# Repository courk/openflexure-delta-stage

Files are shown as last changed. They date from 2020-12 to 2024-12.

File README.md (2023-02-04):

# OpenFlexure Delta Stage

A 3D Printable high-precision 3-axis delta-bot translation stage.

This project is a 3D printable design that enables very fine (sub-micron) mechanical positioning of a small moving stage, with surprisingly good mechanical stability.  It follows on from the [OpenFlexure Microscope](https://openflexure.org/projects/microscope/). The main advantage of this design is that the optics remain in a fixed position, allowing more complex and heavier optics modalities, as well as coupling into external optics.  

We have described the OpenFlexure Delta Stage's design and possible optical configurations in [Optics Express](https://doi.org/10.1364/OE.450211).

## Printing and building it

The [Delta Stage home page](https://openflexure.org/projects/deltastage/) is the best place to start with making your own Delta Stage.

### Assembly instructions

The [assembly instructions](https://build.openflexure.org/openflexure-delta-stage/latest) contain all the STLs you need to download and print, and a bill of materials for the non printed parts.  There is also guidance on 3D printer settings.  

The assembly instructions give a step by step guide to building the Delta Stage, as both a translation stage and a complete microscope (transmission and reflection illumination).

## Software

The Delta Stage can be powered by [Raspbian-OpenFlexure](https://openflexure.org/projects/deltastage/build#install-the-os).  You can control the Delta Stage either on the Raspberry Pi itself or from a different computer using [OpenFlexure Connect](https://openflexure.org/projects/deltastage/install).

## Customising it

You can customise the delta stage to suit your application.  All of the designs are made using [OpenSCAD](https://www.openscad.org/). Currently we use [OpenSCAD 2019.05](https://openscad.org/news.html#20190518).

### Cloning the repository

The Delta Stage repository uses additional git features which can require extra steps. For this reason, it is recommended that you clone it, rather than download it.  

* The repository uses [submodules](https://git-scm.com/book/en/v2/Git-Tools-Submodules) to include parameters, objects and components from the [OpenFlexure Microscope repository](https://gitlab.com/openflexure/openflexure-microscope).

* The repository uses [git-lfs](https://git-lfs.github.com/) for version control of image (and other large) files. If git-lfs is not installed, cloning the repository will only download placeholders of these files.

#### Visual Studio Code

The easiest way to clone the repository is with [Visual Studio (VS) Code](https://code.visualstudio.com/), with [git-lfs installed](https://git-lfs.github.com/).  If you [clone the repository using VS Code](https://code.visualstudio.com/docs/editor/versioncontrol#_cloning-a-repository) these additional features should work automatically.

You can then make changes using VS Code and use OpenScad with the editor hidden and the `automatic reload and compile` option ticked for compiling.

#### Cloning using the command line

1. Download and install [git-lfs](https://git-lfs.github.com/).

2. The easiest way to correctly clone the project is to run:

    ```bash
    git clone --recurse-submodules https://gitlab.com/openflexure/openflexure-delta-stage.git
    ```

    If the `openflexure-microscope` folder is empty, you should run the following in the main `openflexure-delta-stage` folder:
    1. `git submodule init` (to set the repository up for the first time).
    2. `git submodule update` (to fetch the required data).

 > With git-lfs installed, git will download the latest version of the large files.  If they are still missing run:

```bash
git lfs fetch 
git lfs checkout
```

  > To make Git always download everything in the repository run the following commands in your terminal:

```bash
git config --local lfs.fetchexclude ""
git lfs fetch
git lfs checkout
```

### Downloading the repository

1. Download the `openflexure-delta-stage` repository.
2. In the OpenFlexure Delta Stage repository on GitLab, click on the 8 characters (the commit ref) after the `@` on the folder named `openflexure-microscope @ ...`. This will take you to the OpenFlexure Microscope repository at the correct commit.
     > :warning: It is important that the submodule is at the correct commit, it will not work if it is on a different commit.
3. Download the OpenFlexure Microscope repository and copy these files in the folder called `openflexure-microscope` in the Delta Stage folder.

### Guide to repository

#### Delta Stage components

The Delta Stage components are found in the `openscad` folder. For example the main body is compiled from `openscad/delta_stage.scad`.  The majority of parameters reside in `openscad/parameters.scad`, so you can easily change aspects of the design (height etc.). Some parts of the design borrow objects from the `openflexure-microscope` submodule.

> :warning: There are currently issues where OpenSCAD runs out of memory when previewing or compiling `delta_stage.scad` in the graphical interface. The complexity of the model will be reduced to fix this, but in the meantime it is still possible to compile it using the [command line](https://en.wikibooks.org/wiki/OpenSCAD_User_Manual/Using_OpenSCAD_in_a_command_line_environment#Command_line_usage):

```bash
openscad -o delta_stage.stl delta_stage.scad
```

#### OpenFlexure Microscope components

The `openflexure-microscope` folder is a submodule containing a version of the [OpenFlexure Microscope repository](https://gitlab.com/openflexure/openflexure-microscope) at a specific commit. The components common to both devices are compiled from there.  If you make changes to these components that you feel should be merged in for others to use, then you should make a merge request to that repository (bearing in mind that it will be ahead of the specific commit that this repository uses).

#### Building the components

To build every component you can run ``build.sh`` if you have a Bash shell (in either linux or Windows Subsystem Linux).  You may need to add ``openscad`` to your path if you want this to work in MinGW on Windows, or in the Mac OS Terminal.

It is also useful to look in ``build.sh`` to see how the components are compiled (and from which OpenSCAD file) as some use command line variables.

#### Writing assembly instructions

The [assembly instructions](https://build.openflexure.org/openflexure-delta-stage/latest) cover the standard uses for the delta stage. They are compiled using [gitbuilding](https://gitbuilding.io/) and stored in the `\docs` folder.

### Release flow

We use the [OpenFlexure workflow](https://openflexure.org/contribute/) for development.

We use GitLab CI to manage builds and deployment.

The CI will build STL files that will remain on GitLab for 1 week when:

* A merge request is submitted
* A merge request is modified

The CI will build and deploy STL files and documentation to [build.openflexure.org](https://build.openflexure.org/openflexure-delta-stage) when:

* A build is manually triggered from GitLab web
* A release is tagged

The build server will mark a release as "latest"( [build.openflexure.org/openflexure-delta-stage/latest](https://build.openflexure.org/openflexure-delta-stage/latest) ) when a release is tagged, with a full semantic version and no suffix. For example:

* v6.0.0 will replace "latest"

However, incomplete semantic versions will not replace latest. For example:

* v6.0.1-beta.1 will **not** replace "latest" (pre-release suffix)
* v6.1 will **not** replace "latest" (no patch version specified)
* 6.0.1a will **not** replace "latest" (non-standard suffix)

## Get Involved

It'll be great if you are able to contribute to the OpenFlexure Delta Stage. If you have any issues, questions or suggestions we would love to hear them.

You can:

* Join the discussion in the [forum](https://openflexure.discourse.group/).
* Make an [issue](https://gitlab.com/openflexure/openflexure-delta-stage/-/issues/new).
* Make a merge request.
* [Tweet us](https://twitter.com/openflexure) with your completed projects.

## License

This project is open-source and is released under the CERN open hardware license.  There is not yet any accompanying software, but if that changes please consider it GPL.  Any documentation contained in this project is licensed CC-BY International 4.0.  We are working on selling kits through OpenFlexure Industries, though we're not yet taking orders - however this will stay a fully open-source project.

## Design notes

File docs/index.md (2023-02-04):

# OpenFlexure Delta Stage

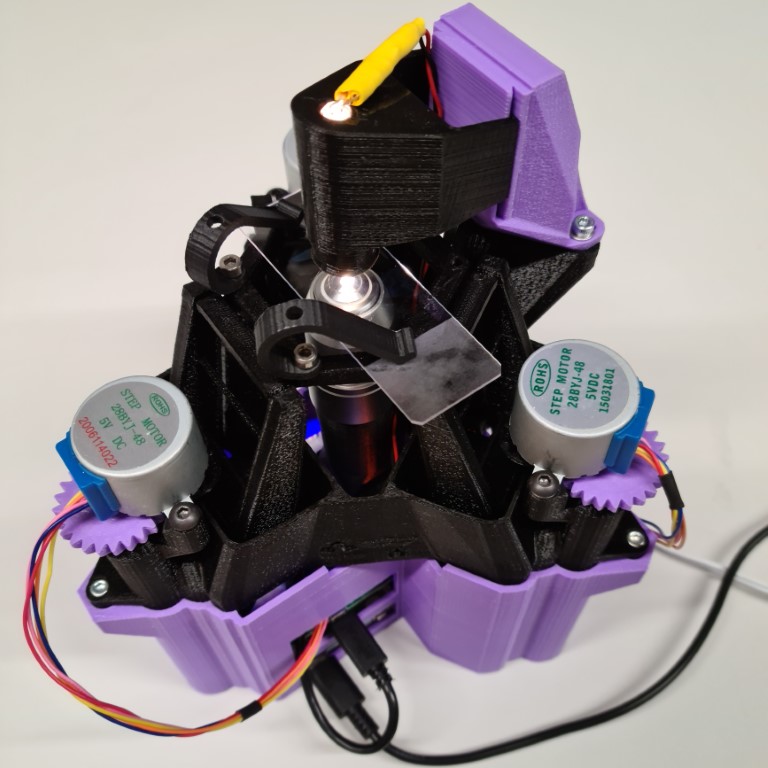
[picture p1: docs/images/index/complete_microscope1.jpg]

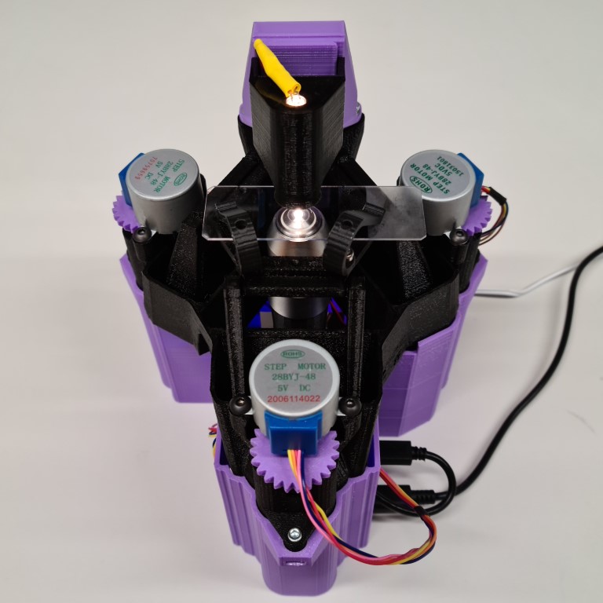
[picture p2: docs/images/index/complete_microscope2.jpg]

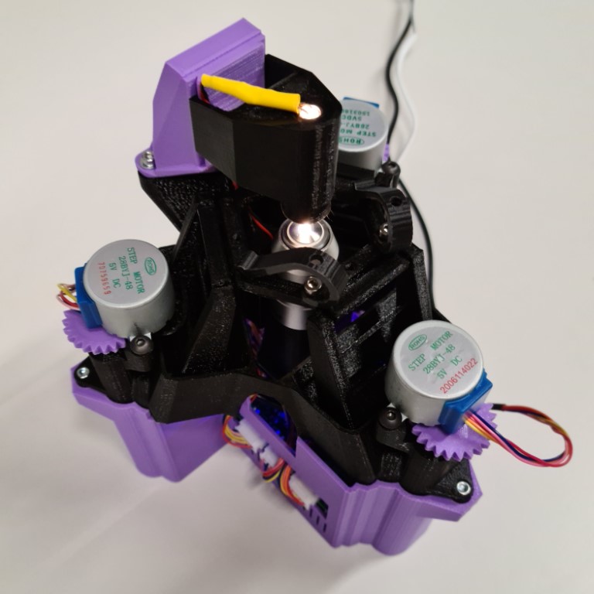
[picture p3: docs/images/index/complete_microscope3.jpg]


The delta stage is a 3D printed x-y-z translation stage. As the optics do not move it is particularly suited to more complex imaging (phase, reflection, fluorescence microscopy).  There are two standard ways to build it, with either transmission illumination or reflection illumination.  The motorised translation stage, which forms the main body of the microscope, is the same for both, and so swapping between the two configurations is possible by replacing the optics module.  There are also some optional components linked at the bottom of the page.

## Publications

We have described the OpenFlexure Delta Stage's design and possible optical configurations in [Optics Express](https://doi.org/10.1364/OE.450211). You can find more related publications and media articles on the [OpenFlexure website](https://openflexure.org/about/media-publications).

## Printing guidance

We normally print with PLA using a 0.15 layer height and ~18% infill. You should not need to print any of the parts with adhesion settings (brim etc.) or supports.  Take note of the optics parts we recommend you print with black PLA, to reduce stray light.

## Building the Delta Stage

There are two versions of the instructions:

* [Delta stage microscope with transmission illumination](pages/index_transmission.md)
* [Delta stage microscope with reflection illumination](pages/index_reflection.md)

### Optional components

* [Simple base](pages/simple_base.md):  Base with nothing inside; matches the footprint of the OpenFlexure Delta stage exactly.
* [Infinity corrected transmission optics module casing](models/optics_picamera2_rms_infinity_f50d13_delta.stl){previewpage}: If you are using infinity corrected objective lenses, you will need to use this version of the optics module casing.  
* [Stage adapters](pages/stage_adapters.md): Adapters for the stage to hold different components.
* [LED Grid illumination](pages/LED_grid_illumination.md): For more complex illumination.

### Software

You can control your microscope using the [OpenFlexure software](https://openflexure.org/projects/microscope/install). The geometry of the Delta Stage is different to the standard OpenFlexure Microscope.  So that the movement of the stage is correct, you will need to change the stage configuration:

1. In OpenFlexure Connect, when connected to your Delta Stage microscope, click `Settings`.
2. Under `MICROSCOPE SETTINGS`, click `Stage`.
3. Change the `Stage geometry` dropdown to `SangaStage (Delta)`.
4. Click `CHANGE STAGE GEOMETRY`.

## Design notes

* [Stage geometry](pages/stage_geometry_notes.md)

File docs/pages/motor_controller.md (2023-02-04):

# Motor controller (Sangaboard)

The stage can be powered by a Raspberry Pi and a motor controller.

{{BOM}}

[Raspberry Pi power supply]: ../components/raspi_power.md "{cat:part}"
[red 4A instrument wire]: ../components/4A_instrument_wire.md#red "{cat:part}"
[black 4A instrument wire]: ../components/4A_instrument_wire.md#black "{cat:part}"
[4.8mm heat shrink]: ../components/4_8mm_heat_shrink.md "{cat:part}"
[6.4mm heat shrink]: ../components/6_4mm_heat_shrink.md "{cat:part}"
[soldering iron]: "{cat:tool}"
[wire stripper]: "{cat:tool}"
[craft knife]: "{cat:tool}"
[heat gun]: "{cat:tool}"
[wire cutters]: "{cat:tool}"

# Method

## The Sangaboard {pagestep}

[These instructions](https://build.openflexure.org/openflexure-microscope/v6.1.5/docs/#/6_motor_controllers) show the different ways of controlling the motors. The base currently works with the Sangaboard v0.2 and v0.3.

## Powering the motors for Sangaboard v0.2 {pagestep}

Do not power the motors from the pins on the Raspberry Pi.  Instead split the [Raspberry Pi power supply] cable.  

Cut the [Raspberry Pi power supply]{qty:1} cable approximately 20cm from the USB plug end using [wire cutters]{qty:1}.

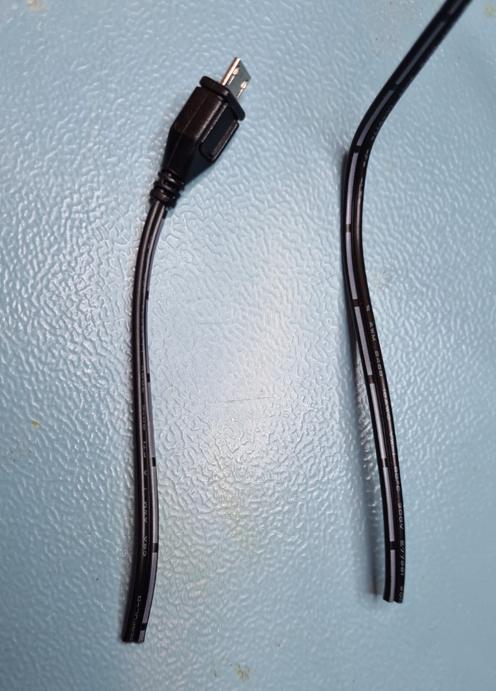
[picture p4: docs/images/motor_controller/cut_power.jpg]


Carefully separate the two cables using a [craft knife]{qty:1} on the USB plug cable for approximately 3cm and strip both wires using a [wire stripper]{qty:1}. Check which wire is positive and negative.  On this official [Raspberry Pi power supply] cable, the wire with long lines printed on is the negative wire.

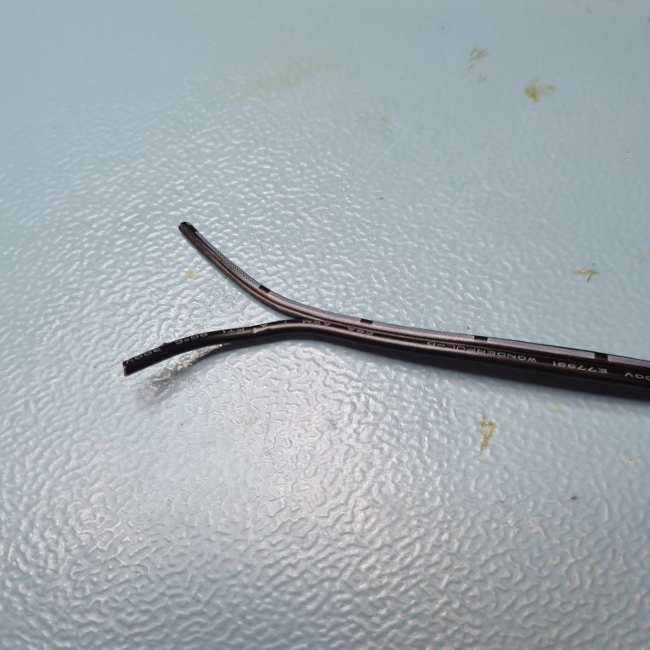
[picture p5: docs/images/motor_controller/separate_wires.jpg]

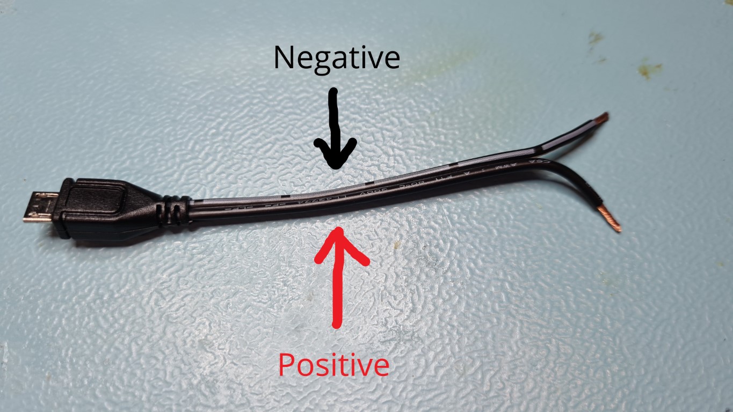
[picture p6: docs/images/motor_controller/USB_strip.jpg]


Cut a 20cm length of [red 4A instrument wire]{qty:20cm} and [black 4A instrument wire]{qty:20cm} using [wire cutters]{qty:1}. Strip one end using a [wire stripper]. Wrap the red wire around the positive wire of the [Raspberry Pi power supply] cable. Solder in place with a [soldering iron]{qty:1} and [solder]{qty:some}.

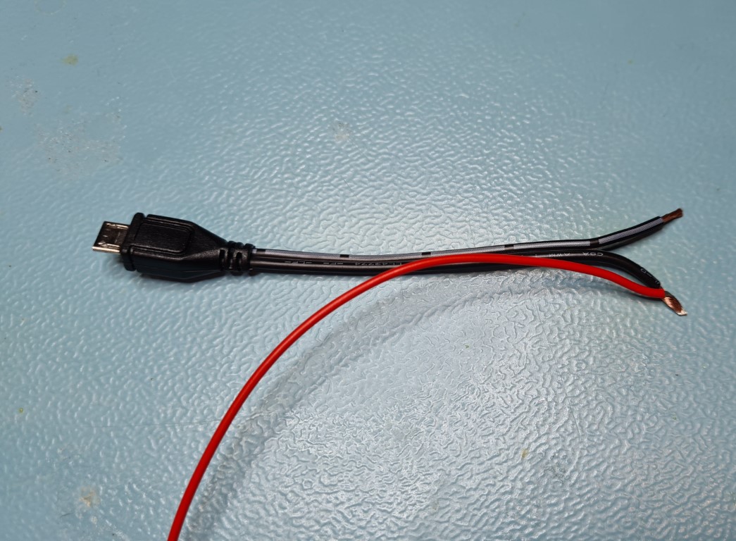
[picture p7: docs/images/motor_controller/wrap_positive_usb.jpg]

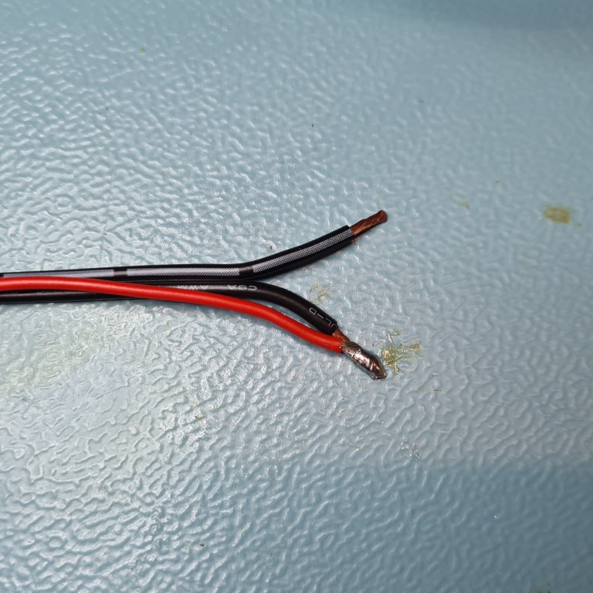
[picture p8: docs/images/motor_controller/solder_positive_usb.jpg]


Repeat for the [black 4A instrument wire] on the negative wire of the [Raspberry Pi power supply] cable.

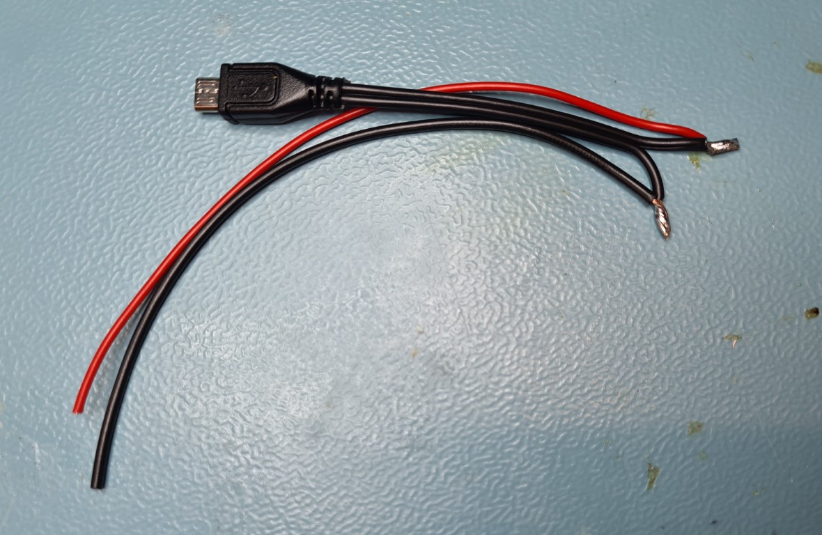
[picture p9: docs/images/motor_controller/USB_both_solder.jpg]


Cut two [4.8mm heat shrink]{qty:6cm} tubes approximately 3cm long.  Cut one [6.4mm heat shrink]{qty:6cm} tube approximately 6cm long.

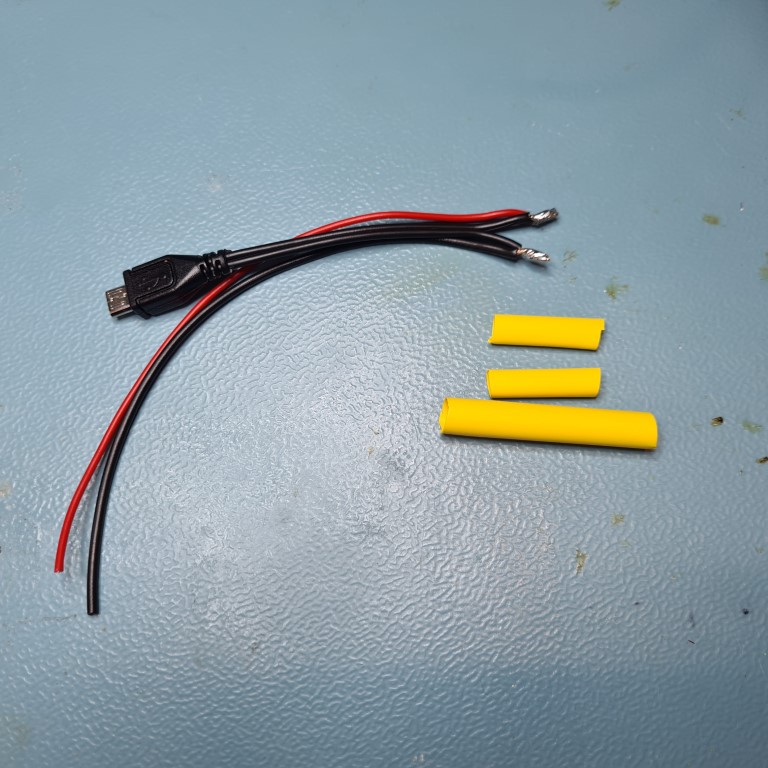
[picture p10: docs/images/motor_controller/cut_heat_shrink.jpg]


Carefully separate the two cables using a [craft knife]{qty:1} on the longer end of the [Raspberry Pi power supply] cable for approximately 5cm and strip both wires using a [wire stripper]. Push the longer [6.4mm heat shrink] tube over both wires and the two shorter [4.8mm heat shrink] tubes over each of the wires.

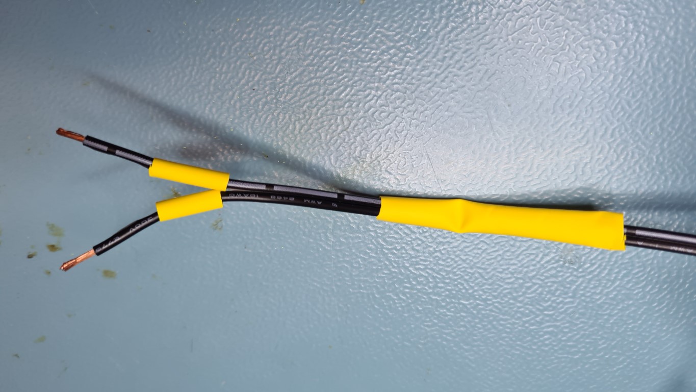
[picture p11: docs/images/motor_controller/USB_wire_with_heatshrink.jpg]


Wrap the negative wire from the longer cable with the already soldered negative wire from the USB end.  Solder in place with a [soldering iron]{qty:1} and [solder]{qty:some}.

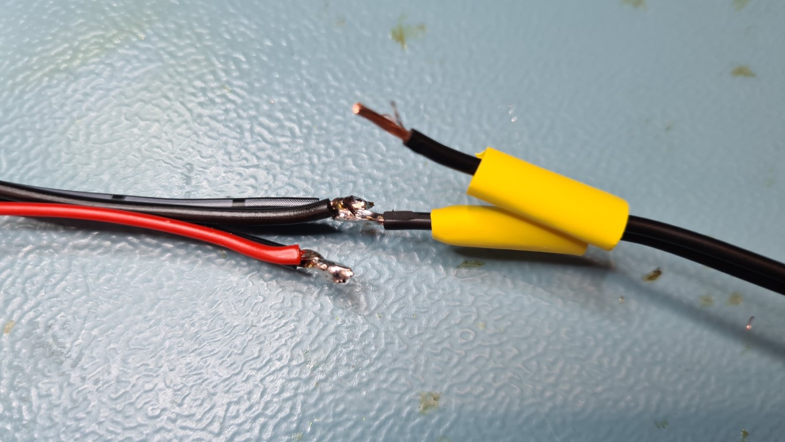
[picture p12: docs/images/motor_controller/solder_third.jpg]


Repeat for the positive wire.

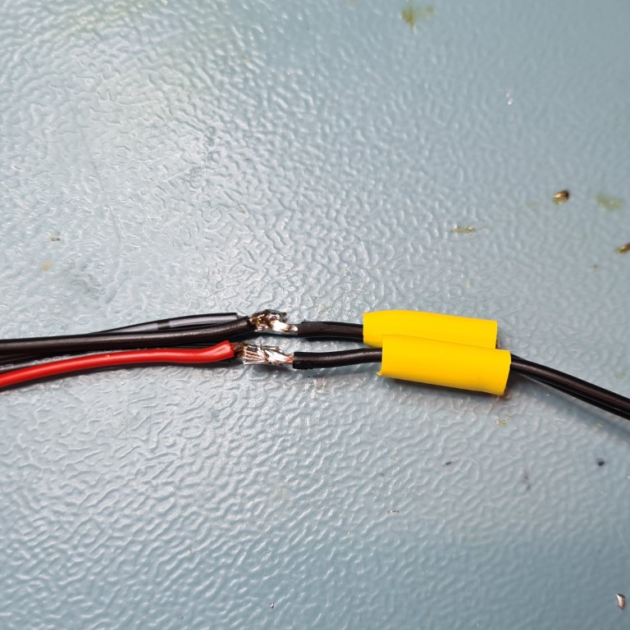
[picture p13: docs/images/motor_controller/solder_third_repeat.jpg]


Move the two [4.8mm heat shrink] tubes over the joints and heat in place using a [heat gun]{qty:1} or [soldering iron]{qty:1}.

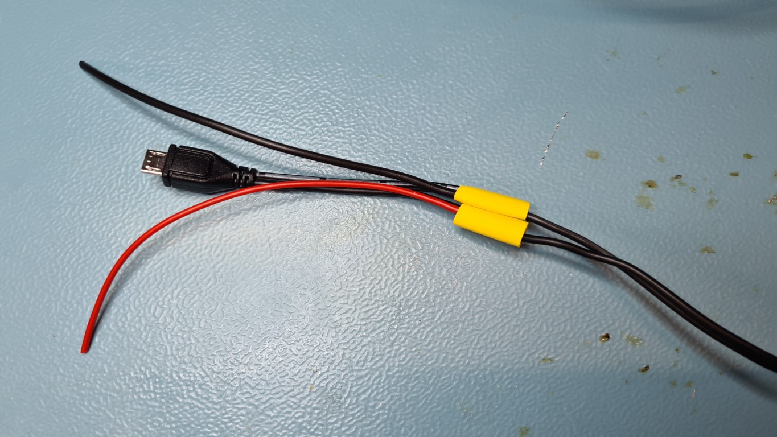
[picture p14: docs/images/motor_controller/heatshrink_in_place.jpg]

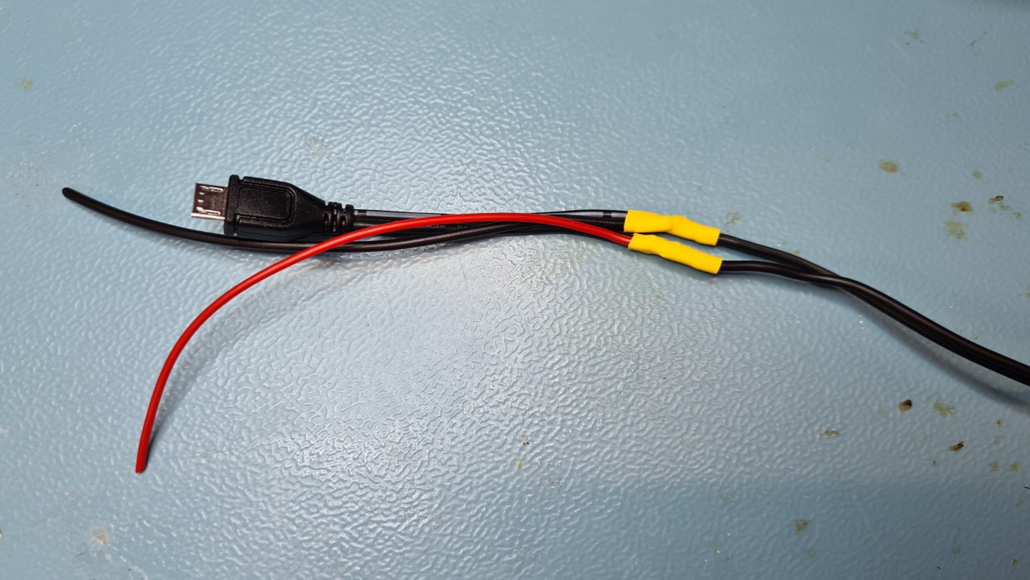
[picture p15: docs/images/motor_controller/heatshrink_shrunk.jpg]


Move the [6.4mm heat shrink] tube over both joints and heat in place using a [heat gun]{qty:1} or [soldering iron]{qty:1}.

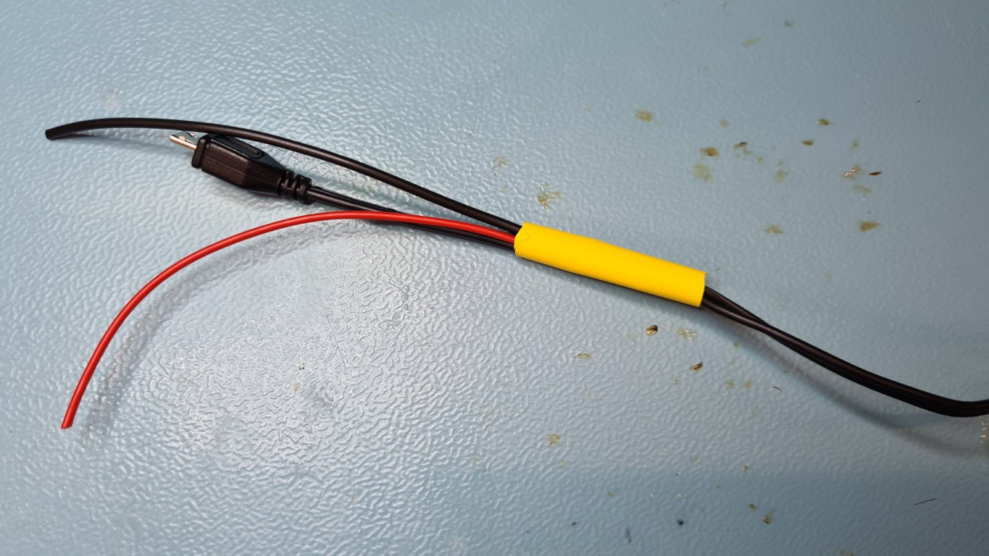
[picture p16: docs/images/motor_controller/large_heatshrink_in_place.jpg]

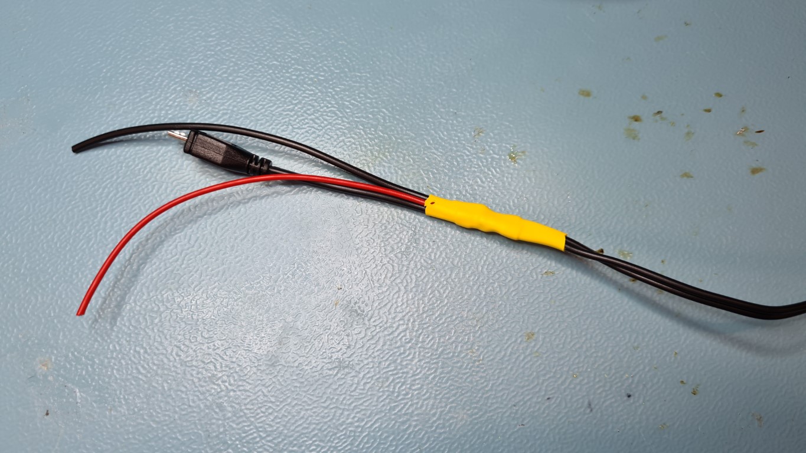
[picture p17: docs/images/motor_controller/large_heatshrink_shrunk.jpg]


You can then attach the connector of your choice to connect to the Sangaboard v0.2.

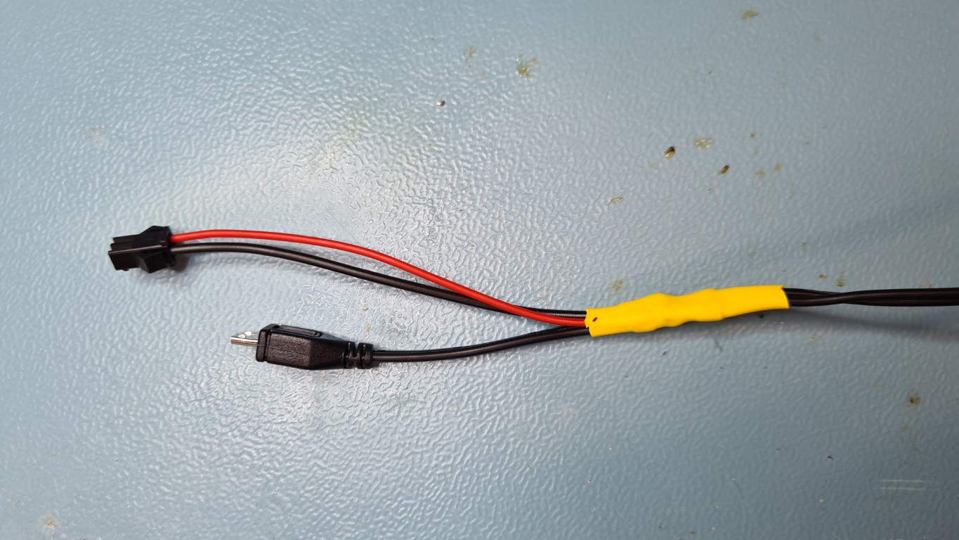
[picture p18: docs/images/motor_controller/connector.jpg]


## Powering the motors for Sangaboard v0.3 {pagestep}

The Sangaboard v0.3 is powered by micro USB.  It should not be powered from a USB port on the Raspberry Pi, but by a separate power source.

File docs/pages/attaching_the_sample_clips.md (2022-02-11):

# Attaching the sample clips

To securely hold a microscope slide on the stage, you can attach the sample clips.

{{BOM}}

[sample clip]: ../models/sample_clips.stl "{cat: 3DPrinted, note: Both sample clips are in the one file.}"
[M3x6mm screw]: "{cat:part}"

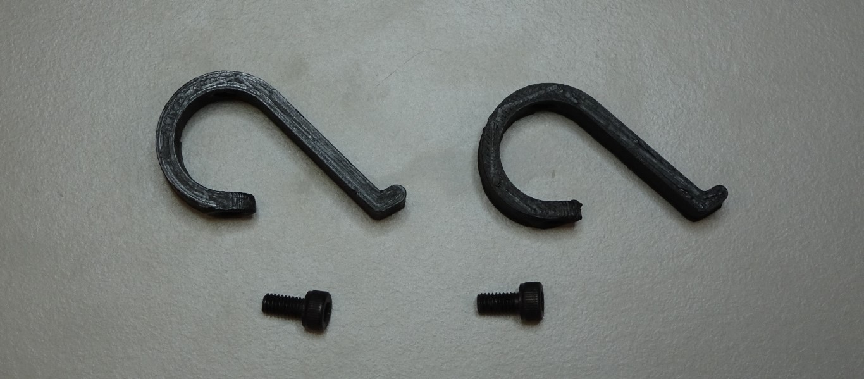
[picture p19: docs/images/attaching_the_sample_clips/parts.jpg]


[2.5mm hex screwdriver]: "{cat:tool}"

# Method

## Insert the screws into the clips {pagestep}

Push the two [M3x6mm screw]{qty:2}s through the lower hole of the [sample clip]{qty:2} using a [2.5mm hex screwdriver]{qty:1}.  

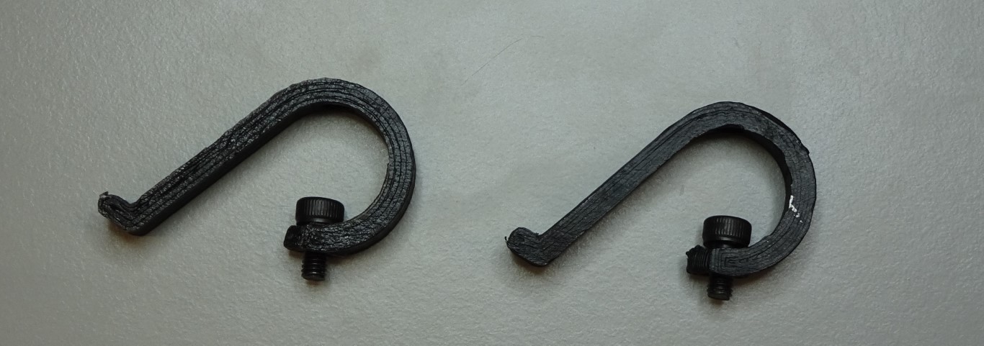
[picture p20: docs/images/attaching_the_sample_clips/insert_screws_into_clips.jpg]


## Screw the sample clips onto the stage {pagestep}

There are 9 holes on the top of the stage, allowing you flexibility when choosing where to place the sample clips. Screw the sample clip to the stage, going through the hole at the top.  

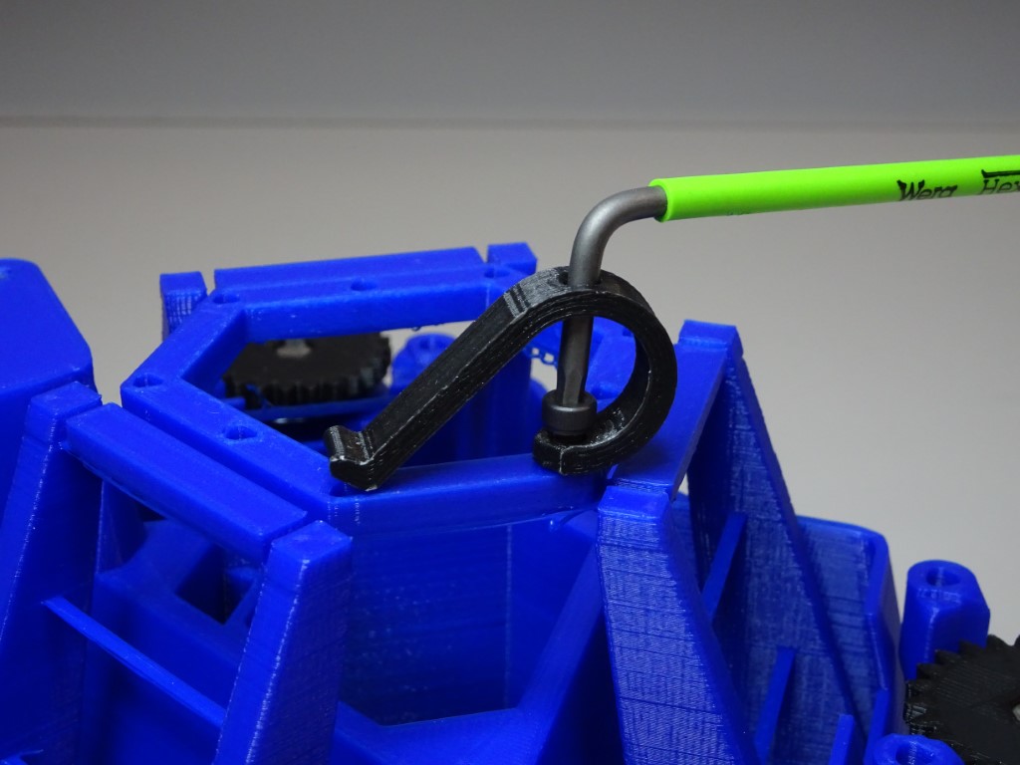
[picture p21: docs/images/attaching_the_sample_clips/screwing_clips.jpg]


If it is difficult to start screwing, then you may find it useful to tap the hole with the screw first.  

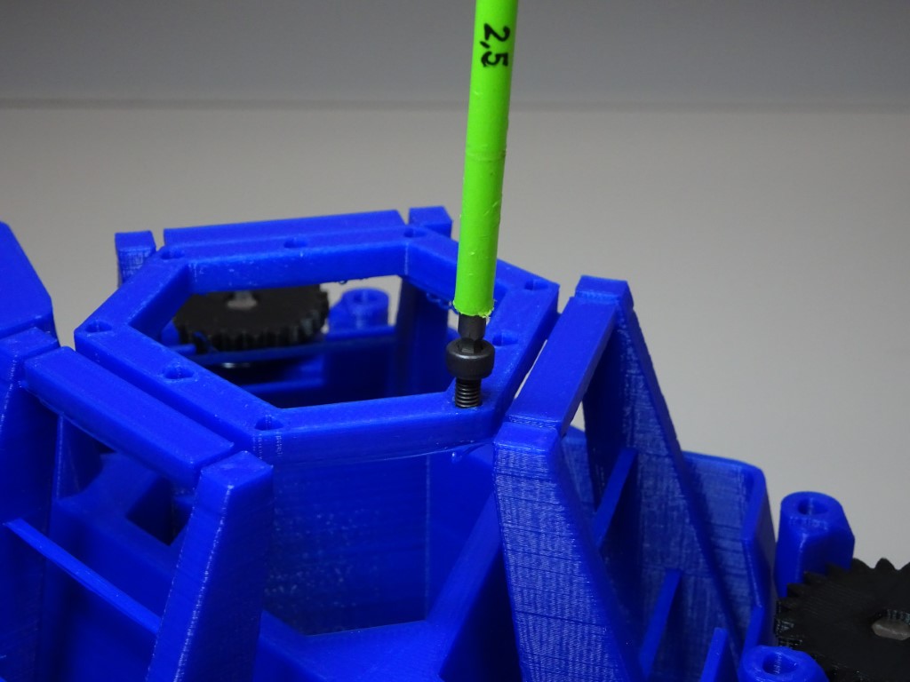
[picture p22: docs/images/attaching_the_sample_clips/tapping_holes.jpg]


Attach the second clip in the same way.  

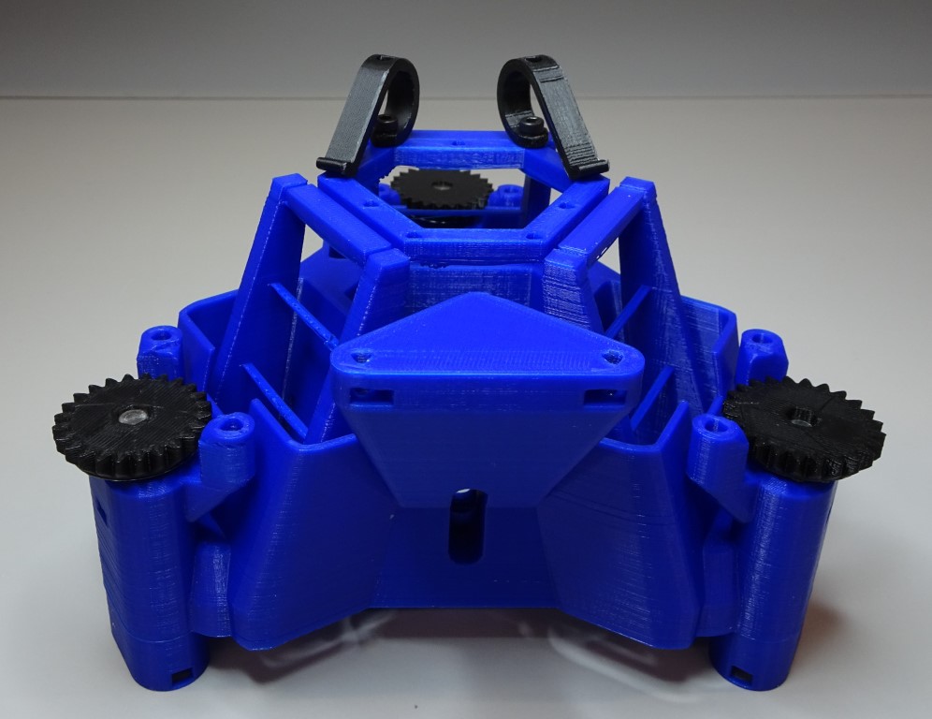
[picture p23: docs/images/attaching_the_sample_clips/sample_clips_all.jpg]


## Clamp the slide {pagestep}

Now you can gently lift up the glass clips and place your microscope slide.  

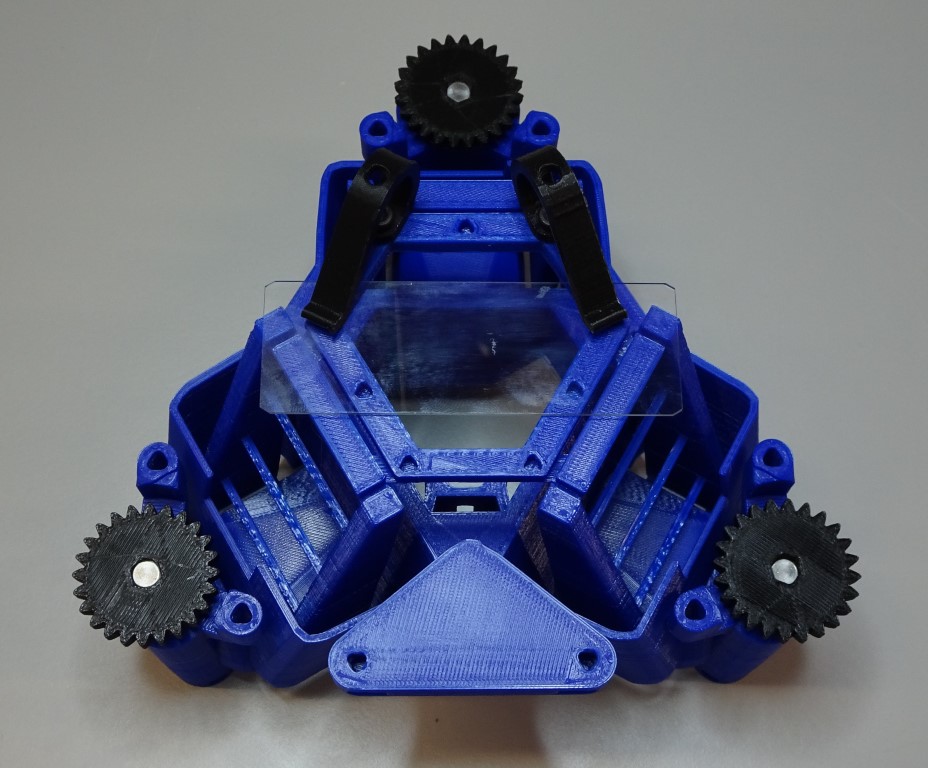
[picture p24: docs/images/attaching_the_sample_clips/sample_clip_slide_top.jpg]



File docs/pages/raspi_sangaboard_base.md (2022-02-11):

# Raspberry Pi and Sangaboard base

This base fits both the Raspberry Pi (Models B+, 2, 3B, 3B+, 4B) and the Sangaboard (v0.2 and v0.3), with holes for the wires and connections and space for an optics module to move.

>**Warning:** Make sure your SD card is flashed with the [OS and software](../index.md#Software) and inserted into your Raspberry Pi.

{{BOM}}

[Raspberry Pi & Sangaboard base]: ../models/base_raspi_sangaboard.stl "{cat: 3DPrinted}"
[M2.5x20mm standoff]: ../components/20mm_standoffs.md "{cat:part}"
[M2.5x8mm screw]: "{cat:part}"
[M3x12mm screw]: "{cat:part}"
[M3 nut]: "{cat:part}"
[Raspberry Pi]: ../components/raspberry_pi.md "{cat:part}"
[Sangaboard]: ../components/sangaboard.md "{cat:part}"
[USB cable]: ../components/sangaboard_USB_cable.md "{cat:part}"
[main body]: ../components/delta_stage_main_body.md "{cat:3DPrinted}"
[small pliers]: "{cat:tool}"
[SW5 nut driver]: "{cat:tool}"
[2mm hex screwdriver]: "{cat:tool}"
[2.5mm hex screwdriver]: "{cat:tool}"

# Method

## Base stabilisation {pagestep}

You may wish to add [rubber feet]{qty:3} to your [Raspberry Pi & Sangaboard base]{qty:1} for stability.




Alternatively, you could sit it on a layer of foam or drill holes in the bottom of the base to attach it to an optical bench.

## Add Raspberry Pi {pagestep}

Connect the camera ribbon cable and LED to the [Raspberry Pi]{qty:1}. The LED should connect with the positive (red) cable to the 5V pin (number 4) and the ground (black) cable to the Ground pin (number 6) on the [GPIO](https://www.raspberrypi.org/documentation/usage/gpio/).

Place the [Raspberry Pi] into the bottom of the case.  Screw the four [M2.5x20mm standoff]{qty:4}s through the holes of the Raspberry Pi (hand tight or using [small pliers]{qty:1} or [SW5 nut driver]{qty:1}, being careful not to over-tighten) and into the base.  You may find it easier to tap the holes with M2.5 screws before.




## Add Sangaboard {pagestep}

Place the [Sangaboard]{qty:1} on top of the standoffs, making sure the cables from the Raspberry Pi have space. The LED cable can exit the through the window at the back.  

### Sangaboard v0.2

Screw the [M2.5x8mm screw]{qty:4}s using a [2mm hex screwdriver]{qty:1} through the holes of the Sangaboard into the standoffs. You might find it easier to attach all four loosely, then tighten them together. Be careful not to over-tighten these screws.





### Sangaboard v0.3

You can attach this Sangaboard to the two standoffs closest to the GPIO with two [M2.5x8mm screw]s using a [2mm hex screwdriver]{qty:1}.  It will sit (but not secured) on the other two standoffs.




## Plug in motors {pagestep}

Plug in the motors.  Motor cables from motors `a` and `b`  can enter though the window in the side of the case and the motor cable from motor `c` can enter through the window at the back or the side. The correct order to plug in the motors can be seen here:

### Sangaboard v0.2




### Sangaboard v0.3




(For other motor controllers: `a = x`, `b = y`, `c = z`)

## Attach the camera ribbon cable {pagestep}

Connect the ribbon cable to the camera module.



## Put microscope into base {pagestep}

The microscope [main body] fits tightly into the [Raspberry Pi & Sangaboard base].



## Secure the microscope to the base {pagestep}

Insert one [M3 nut]{qty:3} into the nut trap in the base.  It may be necessary to clear out the hole of printing artefacts.  




Insert one [M3x12mm screw]{qty:3} into the hole in the microscope [main body].  Screw it in place using a [2.5mm hex screwdriver]{qty:1}.





Repeat for the other two base connectors.





## Connect the Sangaboard {pagestep}

The Sangaboard connects to the Raspberry Pi from the Arduino USB port by [USB cable]{qty:1}. There is a special window for the USB cable to pass through.

### Sangaboard v0.2




### Sangaboard v0.3





## Attach external components {pagestep}

There are windows around base to connect external components.  On the side there is space for USB power to the Raspberry Pi and Sangaboard v0.2 and HDMI.




At the back there is space for USB components (for example: keyboard, mouse, memory stick), ethernet and power supply for the Sangaboard v0.3.




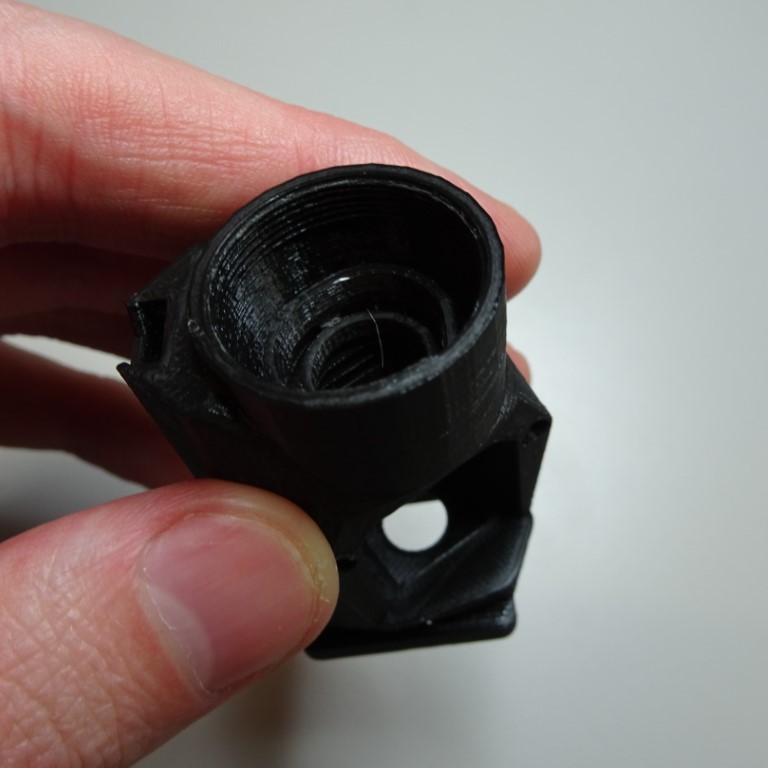
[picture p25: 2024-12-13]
docs/images/reflection_illumination/clean_optics1.jpg

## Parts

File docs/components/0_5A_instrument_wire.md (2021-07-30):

# 0.5A Instrument wire

10/0.1mm Instrument wire (0.5A)

## Black

e.g. Rapid [01-1500](https://www.rapidonline.com/rapid-gw011500-10-0-1mm-equipment-wire-black-100m-01-1500)

## Red

e.g. Rapid [01-1535](https://www.rapidonline.com/rapid-gw011535-10-0-1mm-equipment-wire-red-100m-01-1535)

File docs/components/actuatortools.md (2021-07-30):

# Actuator tools  

All three components are in the same file.

## Band tool

[Actuator assembly tools](../models/actuator_assembly_tools.stl){previewpage}

## Band tool holder

[Actuator assembly tools](../models/actuator_assembly_tools.stl){previewpage}

## Nut tool

[Actuator assembly tools](../models/actuator_assembly_tools.stl){previewpage}

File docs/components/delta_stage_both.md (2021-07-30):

# Delta Stage main body

This is just the stage, without the reflection illumination hole and transmission illumination condenser mount.

> **Warning:** You should not print the Delta Stage main body using a brim as it will interfere with the mechanism.  Instead use the smart brim version.

## Delta Stage

Delta Stage

## Delta Stage smart brim

Delta Stage smart brim

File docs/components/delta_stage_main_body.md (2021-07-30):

# Main body

[Delta Stage main body]: ./delta_stage_both.md "{cat:3DPrinted}"
[Delta Stage Microscope main body]: ./delta_stage_microscope_both.md "{cat: 3DPrinted}"

There are two options for the main body.

1. If you just want the stage, you will need to print the [Delta Stage main body].
2. If you want to use the Delta Stage Microscope, you will need to print [Delta Stage Microscope main body].

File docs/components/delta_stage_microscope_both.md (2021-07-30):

# Delta Stage microscope main body

This is the body for the complete microscope, with the reflection illumination hole and transmission illumination condenser mount.

> **Warning:** You should not print the Delta Stage Microscope main body using a brim as it will interfere with the mechanism.  Instead use the smart brim version.

## Delta Stage Microscope

Delta Stage Microscope

## Delta Stage Microscope smart brim

Delta Stage Microscope smart brim

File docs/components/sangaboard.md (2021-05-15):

# Sangaboard

[These instructions](https://build.openflexure.org/openflexure-microscope/latest/docs/#/6_motor_controllers) show the different ways of controlling the motors. The base is currently compatible with Sangaboard v0.2 and v0.3.

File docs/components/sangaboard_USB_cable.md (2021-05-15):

# Sangaboard USB cable

Used to connect the Sangaboard to the Raspberry Pi.

Type: USB micro B to USB A.

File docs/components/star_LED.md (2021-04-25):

# Star LED

You will require an LED Engin LZ1 LED with the Starboard.  You should choose which one you require based on the excitation wavelength.

eg. 
<table>
    <tr>
        <th> Colour </th>
        <th> Wavelength (nm) </th>
        <th> Mouser Part no. </th>
    </tr>
    <tr>
        <td> UV </td>
        <td> 365 - 370 </td>
        <td> <a href = "https://www.mouser.co.uk/ProductDetail/LED-Engin/LZ1-10UV0R-0000/?qs=P1JMDcb91o5%252BTa3J2FIx5Q%3D%3D">897-LZ1-10UV0R-0000</a> </td>
    </tr>
        <tr>
        <td> Blue </td>
        <td> 460 </td>
        <td> <a href = "https://www.mouser.co.uk/ProductDetail/LED-Engin/LZ1-10B202-0000?qs=QhAb4EtQfbWOLKWBru6FXA%3D%3D">897-LZ110B2020000</a> </td>
    </tr>
        <tr>
        <td> Green </td>
        <td> 523 </td>
        <td> <a href = "https://www.mouser.co.uk/ProductDetail/LED-Engin/LZ1-10G102-0000?qs=QhAb4EtQfbUZK37Yw6q95g%3D%3D">897-LZ110G102000</a> </td>
    </tr>
        <tr>
        <td> Red </td>
        <td> 623 </td>
        <td><a href = "https://www.mouser.co.uk/ProductDetail/LED-Engin/LZ1-10R102-0000?qs=QhAb4EtQfbUOXmBwg3w3fQ%3D%3D">897-LZ110R1020000</a> </td>
    </tr>
        <tr>
        <td> Cool White </td>
        <td> 5500K </td>
        <td><a href = "https://www.mouser.co.uk/ProductDetail/LED-Engin/LZ1-10CW02-0055?qs=sGAEpiMZZMt82OzCyDsLFC9d7bkTA8Rg4x8j7Nzmv7M%3D">897-LZ110CW020055</a> </td>
    </tr>

</table>

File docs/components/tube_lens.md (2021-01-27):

# Tube lens

* Focal length: 50mm
* Outer diameter: 12.7mm
* Material: glass
* Lens type: cemented achromatic doublet
  
The microscope is designed to use finite-conjugate microscope objectives. However, it is necessary to shorten the distance between the objective and the sensor by inserting a lens in the intervening space. This is not placed one focal length from the camera (as it would be in an infinity-corrected design) and so isn't really a tube lens - think of it as a "tube length correction lens". T  

e.g. ThorLabs part number [AC127-050-A](https://www.thorlabs.com/thorproduct.cfm?partnumber=AC127-050-A)

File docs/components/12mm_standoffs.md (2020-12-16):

# 12mm Standoffs

These raise the Sangaboard above the Raspberry Pi. 

They should be M2.5, with a body length of 12mm, The screw length should be 6mm.  Only steel has been tested.

e.g. Farnell [2884390](https://uk.farnell.com/wurth-elektronik/971120151/standoff-hex-male-female-12mm/dp/2884390)

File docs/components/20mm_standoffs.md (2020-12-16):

# 20mm Standoffs

These raise the Sangaboard above the Raspberry Pi. 

They should be M2.5, with a body length of 20mm, The screw length should be 6mm.  Only steel has been tested.

e.g. Farnell  [2884418](https://uk.farnell.com/wurth-elektronik/971200151/standoff-hex-male-female-20mm/dp/2884418)

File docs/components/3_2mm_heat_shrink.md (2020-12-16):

# 3.2mm heat shrink

3.2mm Sleeve diameter heat shrink tubing with 2:1 shrink ratio.

e.g. RS Stock No. [398-206](https://uk.rs-online.com/web/p/heat-shrink-cold-shrink-sleeves/0398206)

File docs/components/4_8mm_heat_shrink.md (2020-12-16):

# 4.8mm heat shrink

4.8mm Sleeve diameter heat shrink tubing with 2:1 shrink ratio.

e.g. RS Stock No. [398-199](https://uk.rs-online.com/web/p/heat-shrink-cold-shrink-sleeves/0398199)

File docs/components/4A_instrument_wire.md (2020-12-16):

# 2A Instrument wire

16/0.2mm Instrument wire (4A)

## Red

e.g. Rapid [01-0900](https://www.rapidonline.com/rapid-gw010900-100m-reel-black-16-0-2-wire-01-0900)

## Black

e.g. Rapid [01-0935](https://www.rapidonline.com/rapid-gw010935-100m-reel-red-16-0-2-wire-01-0935)

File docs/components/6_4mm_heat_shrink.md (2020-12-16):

# 6.4mm heat shrink

6.4mm Sleeve diameter heat shrink tubing with 2:1 shrink ratio.

e.g. RS Stock No. [417-7261](https://uk.rs-online.com/web/p/heat-shrink-cold-shrink-sleeves/4177261)

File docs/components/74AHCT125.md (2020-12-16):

# 74AHCT125

Quad level shifter (3V-5V)

e.g.
Digikey [296-4655-5-ND](https://www.digikey.co.uk/product-detail/en/texas-instruments/SN74AHCT125N/296-4655-5-ND/375798)

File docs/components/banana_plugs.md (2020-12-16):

# Banana plug

For connecting to 5V power supply for the star LED.

e.g. RS Stock No. [180-6656](https://uk.rs-online.com/web/p/banana-connectors/1806656), [180-6657](https://uk.rs-online.com/web/p/banana-connectors/1806657)

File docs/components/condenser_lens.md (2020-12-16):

# Condenser lens

* Focal length: 5mm
* Outer diameter: 12.7mm
* Material: PMMA

Best sourced in bulk from China.

e.g. Search AliExpress for `pmma lens 5mm` and look for a diameter of 13mm.

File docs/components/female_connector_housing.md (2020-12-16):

# Female connector housing

* 2.54mm pitch
* 2 way, 1 row

Crimp receptacle housing for PCB header connectors.

e.g. RS Stock No. [233-1817](https://uk.rs-online.com/web/p/wire-housings-plugs/2331817)

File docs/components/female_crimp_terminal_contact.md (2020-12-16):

# Female crimp terminal contact

* 20AWG

Female Crimp terminal contact for PCB mount

e.g. RS Stock No. [233-1895](https://uk.rs-online.com/web/p/crimp-contacts/2331895)

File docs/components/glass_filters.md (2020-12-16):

# Glass filters

These will be dependent on your application and you should match their optical characteristics with your fluorophore excitation and emission wavelengths.  We normally buy them in larger glass sheets and cut them down. Our usual supplier in UK is [Comar Optics](https://www.comaroptics.com/components/filters/dichroic-filters).

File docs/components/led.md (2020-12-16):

# LED

* 5mm LED

Our recommendation is a 'warm' LED, to match the wavelength range of a filament bulb, but you can choose one that matches your requirements.

e.g. RS Stock No. [713-3983](https://uk.rs-online.com/web/p/leds/7133983)

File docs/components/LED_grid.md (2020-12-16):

# LED grid

Adafruit DotStar High Density 8x8 Grid - 64 RGB LED Pixel Matrix

Adafruit product ID: [3444](https://www.adafruit.com/product/3444)

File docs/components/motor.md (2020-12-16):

# 28BYJ-48 micro geared stepper motor

*5V

Micro-geared 28BBYJ-48 stepper motor.  Can be obtained from Amazon, eBay, Aliexpress etc.

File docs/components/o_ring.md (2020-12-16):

# O-ring

* Material: Viton (or Nitrile)
* Inner diameter: 30mm
* Cross-section: 2mm
* Outer diameter: 34mm

e.g. [Simply bearings](https://simplybearings.co.uk/shop/p513396/2mm-Section-30mm-Bore-VITON-Rubber-O-Rings/product_info.html)

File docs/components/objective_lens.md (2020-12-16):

# Objective lens

* RMS threaded
* Correction: Plan
* Tube length: 160mm
* Magnification: 4x - 100x

Can be scavenged from old equipment, or obtained cheaply from AliExpress.  We recommend going Plan or Semi-Plan corrected lenses at 40x, and definitely Plan corrected or better at 100x.

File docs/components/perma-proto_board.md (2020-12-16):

# Adafruit Perma-Proto HAT for Pi Mini Kit - No EEPROM

You will need to solder the included GPIO header onto the board to use it as a HAT on top of the Raspberry Pi.

Adafruit Product ID [2310](https://www.adafruit.com/product/2310)

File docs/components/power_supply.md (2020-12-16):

# Power supply

An adjustable bench top DC power supply to power the reflection illumination LED star.

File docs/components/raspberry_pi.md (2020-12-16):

# Raspberry Pi

You will need one model out of B+, 2, 3B, 3B+, 4B. 

You will also need related accessories (SD card, monitor, keyboard, mouse etc.)

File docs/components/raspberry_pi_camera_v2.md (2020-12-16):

# Raspberry Pi Camera v2

The [Raspberry Pi Camera Module v2](https://www.raspberrypi.org/products/camera-module-v2/).

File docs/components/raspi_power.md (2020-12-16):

# Raspberry Pi power supply

We recommend buying the official Raspberry Pi power supply as it supplies a steady 2.5A.

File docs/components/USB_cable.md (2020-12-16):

# USB cable

It will be easiest with a power only USB cable, so that you can expose the positive and negative wires for soldering to the perma-proto board.  You will also need to make sure that it can support 2A.

e.g. Digikey [102-5945-ND](https://www.digikey.co.uk/short/z1424b)

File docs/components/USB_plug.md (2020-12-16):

# USB plug

A 5V USB power supply that can supply up to 2A.

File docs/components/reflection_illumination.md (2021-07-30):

# Reflection Illumination

Both these parts are in the same file.

## Condenser

[reflection illumination](../models/reflection_illuminator_LED_star.stl){previewpage}

## Holder

[reflection illumination](../models/reflection_illuminator_LED_star.stl){previewpage}

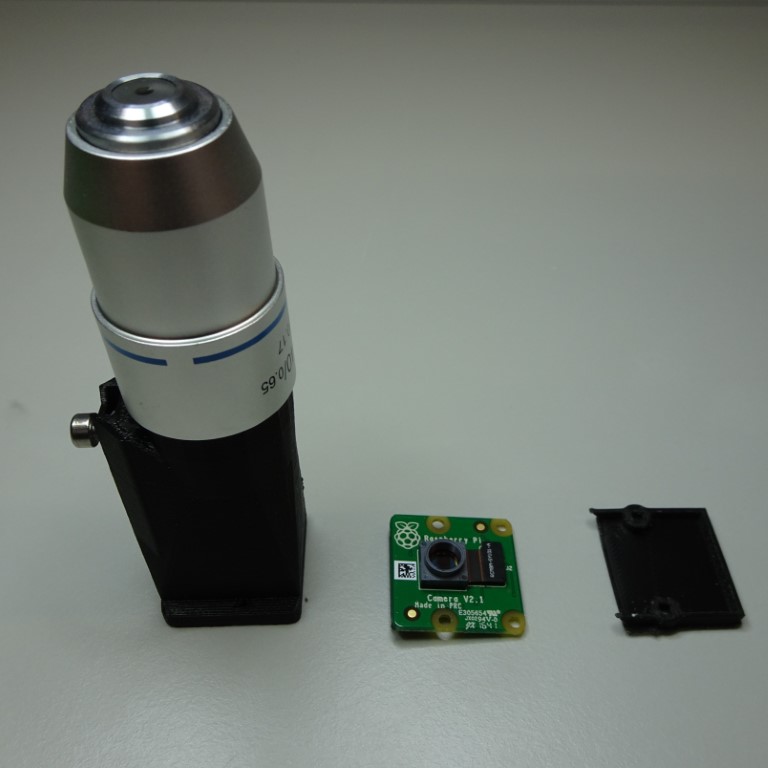
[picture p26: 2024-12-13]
docs/images/transmission_illumination/camera_parts.jpg

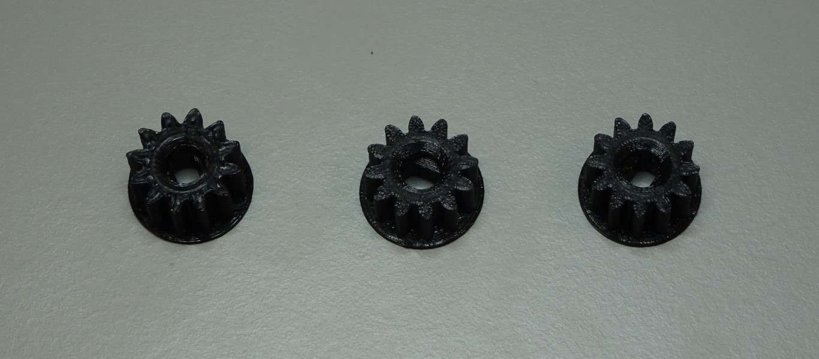
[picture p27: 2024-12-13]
docs/images/attaching_the_motors/printed_parts.jpg

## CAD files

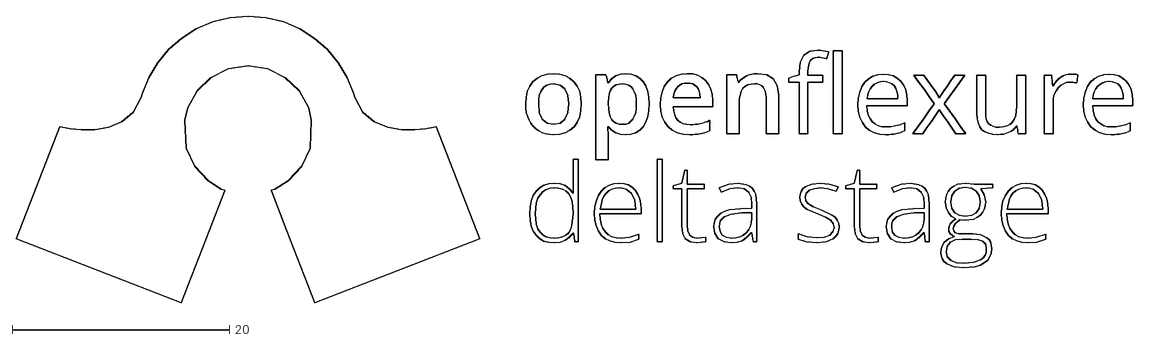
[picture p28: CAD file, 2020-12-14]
openscad/openflexure_delta_stage_logo.dxf
102.8 x 26.4

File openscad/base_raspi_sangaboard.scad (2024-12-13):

include <parameters.scad> //Delta-stage params
use <../openflexure-microscope/openscad/utilities.scad>;
use <../openflexure-microscope/openscad/compact_nut_seat.scad>;
use <delta_stage.scad>
use <delta_stage_logo.scad>;
use <../openflexure-microscope/openscad/logo.scad>;

module base_projection(){
    projection(cut=true){
        union(){
            difference(){
                union(){    // casing around the leg&lever
                    each_lever() minkowski(){
                        leg_and_lever_clearance();
                        cylinder(r1=wall_t, r2=0.5, h=0.9);
                    }
                    reflect([1,0,0]){
                        translate([-(casing_radius+1),0,0])cube([(casing_radius+1),casing_apothem,10]); // This fills in space in the side that are then later cut to give access to side RPi connections.
                    }
                }
                translate([0,sangaboard_center[1]-sangaboard[1]/2,0])cube([100,sangaboard[1],10]); // This squares off the side wall for access to Sangaboard connections
                translate([-(casing_radius+1),2.5,0])cube([(casing_radius+1),casing_apothem,10]); // This squares off the side wall for access to RPi connections
                translate(raspi_center+[0,-(raspi_board[1]+2),-raspi_standoff])cube(raspi_board+[10,0,0],center=true); //This squares off the back wall for access to RPi connections
            }
            // This fills in where the RPi goes with extra space at the front of the microscope as the Sangaboard is bigger that the RPi in that dimension
            translate(raspi_center-[0,-2,raspi_standoff]) cube(raspi_board + [1,8,0], center =true);
        }
    }
}

module feet_projection() {
    projection(cut=true){
        // casing for the actuator
        each_lever() translate([0, nut_y, -49]) screw_seat_shell(h=actuator_h + 99);
    }
}

module base_extrusion(h) {
    linear_extrude(height=h) {
        union() {
            feet_projection();
            base_projection();
        }
    }
}

module base_hollow(cutout_tolerance=1) {
    difference(){
        union(){
        // Base extrusion, but with an outer wall wall_thickness thick
            minkowski(){
                base_extrusion(base_height);
                cylinder(r=wall_thickness+cutout_tolerance,h=1);
            }
            stage_connection();
        }
        // Base extrusion, but with an outer wall cutout_tolerance thick
        translate([0, 0, wall_thickness]) minkowski(){
            base_extrusion(base_height);
            cylinder(r=cutout_tolerance,h=1);
        }
    }
}

module foot_stands(height=base_height, cutout_tolerance=1) {
    // Creates 3 ledges approximately half the foot size such that the main body of the microscope will start 2mm below the height of the base.
    translate([0,0,height-foot_height+1]){
        each_lever(){
            translate([0, nut_y, 0]){
                intersection(){
                    hull(){
                        difference(){
                            minkowski(){
                                linear_extrude(d){
                                    projection(){
                                        screw_seat_shell(10);
                                    }
                                }
                                cylinder(r=cutout_tolerance,h=d);
                            }
                            translate([0,-52.5,0])cube([100,100,100],center = true);
                        }
                        translate([0,10,-20]) cube([30,d,d],center=true);
                    }
                    translate([0,0,-50]){
                        minkowski(){
                            screw_seat_shell(100);
                            cylinder(r=cutout_tolerance+1,h=d);
                        }
                    }
                }
            }
        }
    }
}

//The walls and floor of the base
module base() {
    union(){
        foot_stands(cutout_tolerance=base_cutout_tolerance);
        base_hollow(cutout_tolerance=base_cutout_tolerance);
    }
}

// All the windows to pass cables through
module window_cubes() {
    //RPi windows
    // Back window
    translate(raspi_center+[0,-50,-raspi_board[2]/2+USB_ethernet_window[2]/2-3]) cube(USB_ethernet_window,center=true);

    //Side window
    translate(raspi_center+[-power_HDMI_window[0]/2,raspi_board[1]/2-power_HDMI_window[1]/2-3.5,-raspi_board[2]/2+power_HDMI_window[2]/2-1]) cube(power_HDMI_window,center = true);

    //Vents
    translate([sangaboard_center[0]+50,sangaboard_center[1]+5/2,raspi_center[2]])repeat(delta=[0,(sangaboard[1]-5)/14,0],N=15, center= true) cube([100,1.5,power_HDMI_window[2]],center=true);

    //SD card access
    translate(raspi_center+[0,raspi_board[1]/2+5,-10])cube([20,25,20], center=true);


    //Sangaboard windows
    // Back window
    translate(sangaboard_center-[0,50,0]) rotate([0,0,90])cube(sangaboard_window, center=true);

    //Side windows
    translate([raspi_center[0]-power_HDMI_window[0]/2,raspi_center[1]+raspi_board[1]/2-power_HDMI_window[1]/2-3.5,sangaboard_center[2]-sangaboard[2]/2+power_HDMI_window[2]/2+3]) cube(power_HDMI_window+[0,0,6], center = true);
    translate([raspi_center[0]-power_HDMI_window[0]/2,raspi_center[1]+raspi_board[1]/2-power_HDMI_window[1]/2-3.5,sangaboard_center[2]-sangaboard[2]/2+power_HDMI_window[2]/2+3-10]) cube(power_HDMI_window+[0,0,6], center = true);
    translate(sangaboard_center+[50,5/2,-sangaboard[2]/2+power_HDMI_window[2]/2+3]) cube([100,sangaboard[1]-5,power_HDMI_window[2]+6],center = true);
    //Reflection gap
    rotate([0,0,-60])translate([0,50,base_height-9])cube([bottom_cutout_w,100,20],center=true);
}

module pi_supports(){
    // position supports for each of the pi's mounting screws
    translate(raspi_center+[0,raspi_center[1],-raspi_center[2]]) repeat([49,0,0],2, center=true) repeat([0,58,0], 2,center=true) children();
}

// The four mounting holes underneath the Raspberry Pi.
module raspi_supports(){
    difference(){
        pi_supports() cylinder(h=raspi_standoff, d=7);
        pi_supports() trylinder_selftap(2.5, h=999, center=true);
    }
}

module stage_connection(height=base_height){
    // Creates 3 mounting posts to connect to the main body. The top of the post is in line with the top of the base, with the cutout circle 2mm down such that the main body sits 2mm under the top of the base.
    translate([0,0,height+1])
    {
        each_base_mounting_point(){
            difference(){
                hull(){
                    translate([0,0,-2*d])repeat([0,0,-10],2){
                        minkowski(){
                            cube([10,10,d], center = true);
                            cylinder(r = 1, h = d, $fn = 50);
                        }
                    }
                    translate([0,nut_y+stage_r-mounting_point,-20]){
                        difference(){
                            linear_extrude(20){
                                projection(){
                                    minkowski(){
                                        screw_seat_shell(10);
                                        cylinder(r=wall_thickness,h=d);
                                    }
                                }
                            }
                        translate([-50,-99,-50])cube([100,100,100]);
                        }
                    }
                }
                translate([0,0,-2])cylinder(d = 8.5, h = 2, $fn=50);
                translate([0,0,-8+d])cylinder(d= 3.5, h = 8, $fn=50);
                translate([0,0,-10-8+d])trylinder_selftap(3, h=20, center=true);
                hull()repeat([0,100,0],2) translate([0,0,-8]) cylinder(d=6.9,h=2.8,$fn=6);
            }
        }
    }
}

// Used to show position of sangaboard
module sangaboard(){
    translate(sangaboard_center) cube(sangaboard, center =true);
}

//Used to show position of raspberry pi
module raspi(){
    translate(raspi_center)cube(raspi_board, center = true);
}

module logos(){
    //The OSHW and OpenFlexure logos (goes on back of the base)
    rotate(-90)translate([casing_apothem-3.5,8,base_height*0.7])rotate([90,0,-90])scale([0.2,0.2,1])oshw_logo_and_text(version_numstring);
    mirror([1,0,0])rotate(-90)translate([casing_apothem-3.5,4,base_height*0.8])rotate([90,0,-90])scale([0.2,0.2,1])openflexure_delta_stage_logo();
}
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

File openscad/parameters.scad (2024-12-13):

/*
  Useful settings/parameters for the OpenFlexure fibre stage
*/

use <../openflexure-microscope/openscad/reflection_illuminator.scad>;
version_numstring = "1.2.1+TI";

// Set the overall geometry
leg_strut_l = 32; // inner width of the legs
stage_r = 25; // distance from the centre to the edge of the stage
flex_z1 = 0; // height of lower flexures
flex_z2 = 70; // height of upper flexures

// Thickness of legs
leg_t = 5;

// Set the length of the actuating levers
xy_gain = 2; // ratio of stage motion to Z motion
lever_l = (flex_z2 - flex_z1)/xy_gain;
nut_y = lever_l + 12;

// Motor lugs
motor_lugs = true;

// Condenser mount
transmission_illumination = false;

// Reflection illumination - The hole cut out the side for the reflection illuminator
reflection_illumination = false;

// Stage connectors - the mounts to connect the stage to the base
stage_connectors = false;

//Objective mount - the dovetail for attaching the optics module
optics_module_mount = true;

// Flexure dimensions - good for PLA and ~0.5mm nozzle
zflex = [6, 1.5, 0.75]; //dimensions of flexure
flex_a = 0.1; //angle through which flexures are bent, radians
dz = 0.5; //thickness before a bridge is printable-on

actuator_h = 30; //height of actuator columns (~screw length)
actuator_travel = (nut_y - zflex[1]/2)*flex_a;

wall_t = 1.6;
d=0.05;

// Mounting stuff
// Mounting holes should be 60 degrees out from the legs (i.e. in between)
// If you extend the line of the solid anchor part in the middle (where each leg
// joins the casing) out sideways, to the middle of the vertical part of the
// leg, then take the midpoint of the line joining each pair, that's the hole)
mounting_hole_r = sin(30)*stage_r + sin(60)*(leg_strut_l/2+zflex[1]+leg_t/2);
// The position of the mounting point between the base and main body (from centre at each 120 degree position of the actuators)
mounting_point = 87;

// Objective mount
objective_mount_y = 18; // y position of clip for optics
objective_mount_back_y = stage_r + wall_t; //back of objective mount
objective_mount_nose_w = 6; // width of the pointy end of the mount

sample_z = 65; // height of the top of the stage
z_flexures_z1 = 8; // height of the lower Z flexure
z_flexures_z2 = min(sample_z - 12, 35); // " upper "

// Feet
feet_endstops = false;
foot_height=feet_endstops?15:15; //the endstops need a bit of extra height (or not)
endstop_extra_ringheight=feet_endstops?1:0;

//Casing
casing_height = actuator_h+actuator_travel + 5; //flex_z2-24; //the maximum height of the lever casing and 'joining together' casing
casing_radius = nut_y; //the outside radius (to the point) of the hexagon used to join the casing together

// size of cutout for fl cube
top_cutout_w = stage_r/2 + 2*wall_t; // As big as we can get at height 'wall_h' without bridging a corner
mid_cutout_w = illuminator_width() + 1;
bottom_cutout_w = illuminator_width() + 4;

// Base
wall_thickness = 2;
simple_base_height = 35;
base_height = 80 + 20;
base_cutout_tolerance = 0.5;
raspi_board = [56,85,16]; // The actual size of the RPi
casing_apothem = casing_radius*sqrt(3)/2; // The apothem of the hexagon used to join up the legs
USB_ethernet_window = [raspi_board[0],100,raspi_board[2]+6]; //The back window for the RPi
power_HDMI_window  = [100,45-3.5,14]; //The side window for the RPi
raspi_standoff = 7; //How high the RPi is from the base (governed by the standoff screw size)
sangaboard = [56,68,25]; // The actual size of the Sangaboard
raspi_center = [0,10,raspi_board[2]/2+raspi_standoff]; // Where the centre of the Raspberry Pi is in its final position
standoff_height = 20; //The height of the standoff between the Rpi and the Sangaboard
sangaboard_center = raspi_center+[0,(raspi_board[1]/2-sangaboard[1]/2),(sangaboard[2]/2-raspi_board[2]/2+standoff_height)]; // Where the centre of the Raspberry Pi is in its final position
sangaboard_window = [100,power_HDMI_window[1],20]; // The back window of Sangaboard

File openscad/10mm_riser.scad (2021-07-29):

// Design for a 10mm riser

use <./stage_adaptor_base.scad>;
use <./delta_stage.scad>;
use <../openflexure-microscope/openscad/utilities.scad>;

difference(){
    stage_adaptor_base(height = 10, screws_center = true);
    each_stage_mounting_hole_without_center(z_translate = 0){trylinder_selftap(nominal_d=3, h=999);}
    each_stage_mounting_hole_just_center(z_translate = 2){cylinder(r=3.01, h=999,$fn=100);}
    each_stage_mounting_hole_just_center(z_translate = -1){cylinder(d=3, h=999,$fn=100);}
    cylinder(r=18.5, h=999,$fn=200); //hole for dish
}

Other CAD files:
openscad/35mm_petri_dish_holder.scad
openscad/55mm_petri_dish_holder.scad
openscad/base.scad
openscad/bottom_of_stage.scad
openscad/delta_stage.scad
openscad/delta_stage_logo.scad
openscad/feet.scad
openscad/laser_tube.scad
openscad/simple_base.scad
openscad/stage_adaptor_base.scad
openscad/threads.scad
openscad/z_axis.scad

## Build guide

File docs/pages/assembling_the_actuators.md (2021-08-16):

# Assembling the actuators

These instructions show you how to assemble the actuators, to drive the motion of the stage.

{{BOM}}

[M3 washer]: "{cat:part}"
[light oil]: "{cat:part}"
[O-ring]: ../components/o_ring.md "{cat:part}"
[M3x25mm hex head screw]: "{cat:part}"
[feet]: ../models/feet.stl "{cat:3DPrinted, note: All three feet are in the one file.}"
[large gear]: ../models/large_gears.stl "{cat: 3DPrinted}"
[band tool]:  ../components/actuatortools.md#bandtool "{cat: 3DPrinted_tool}"
[band tool holder]: ../components/actuatortools.md#bandtoolholder "{cat: 3DPrinted_tool}"
[nut tool]:  ../components/actuatortools.md#nuttool "{cat:3DPrinted_tool}"
[wire cutters]: "{cat:tool}"
[craft knife]: "{cat:tool}"
[main body]: ../components/delta_stage_main_body.md "{cat:3DPrinted}"

# Method

## Cut the ties {pagestep}

For printing stability, on the [main body]{qty:1} there are two plastic ties in every actuator.  Cut these out, either using a [craft knife]{qty:1} or [wire cutters]{qty:1}.  

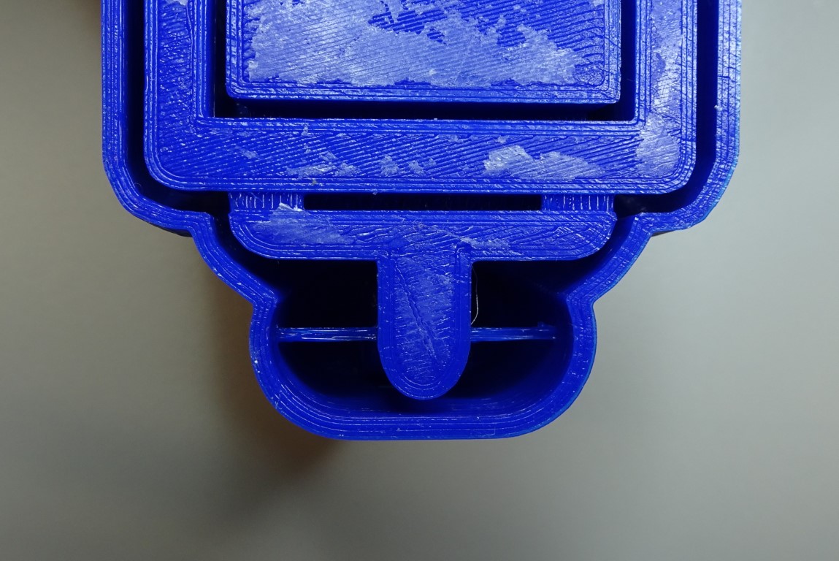
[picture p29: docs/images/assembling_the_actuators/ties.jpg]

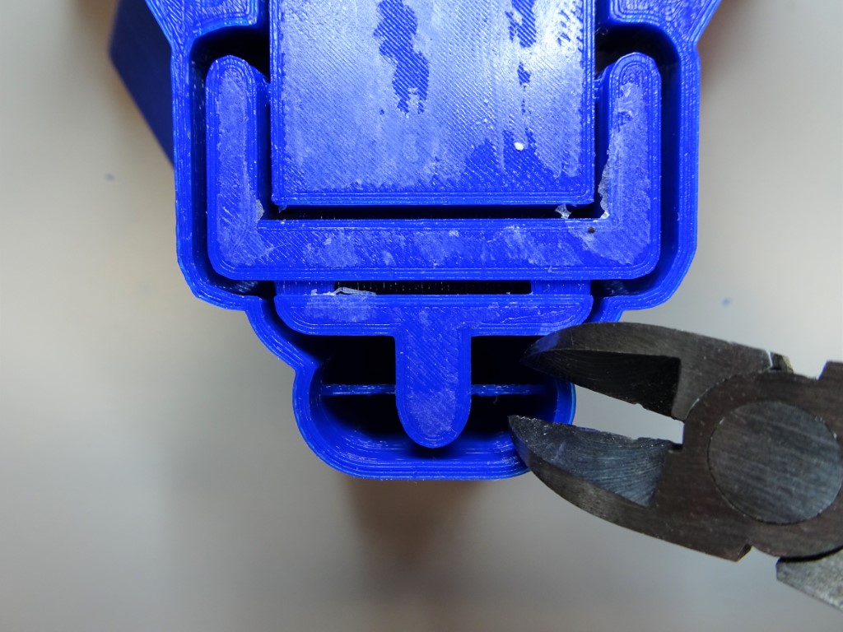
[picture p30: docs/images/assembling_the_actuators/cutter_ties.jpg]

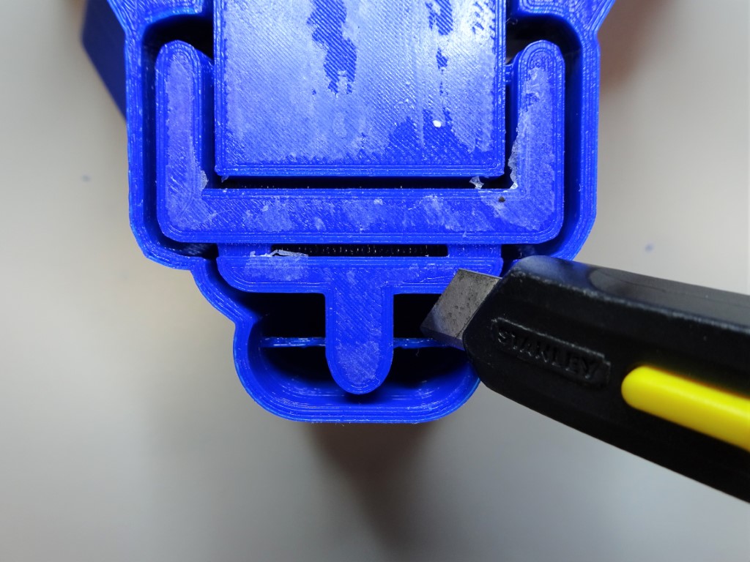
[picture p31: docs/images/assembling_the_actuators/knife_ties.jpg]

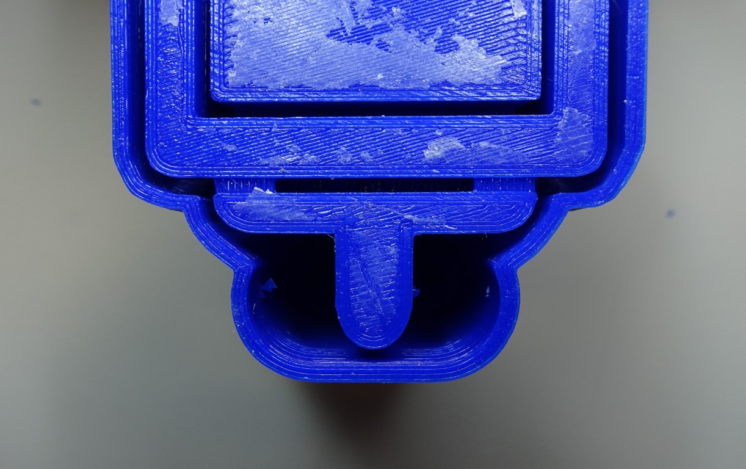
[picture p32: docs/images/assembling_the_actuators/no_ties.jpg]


Repeat for all three actuators.
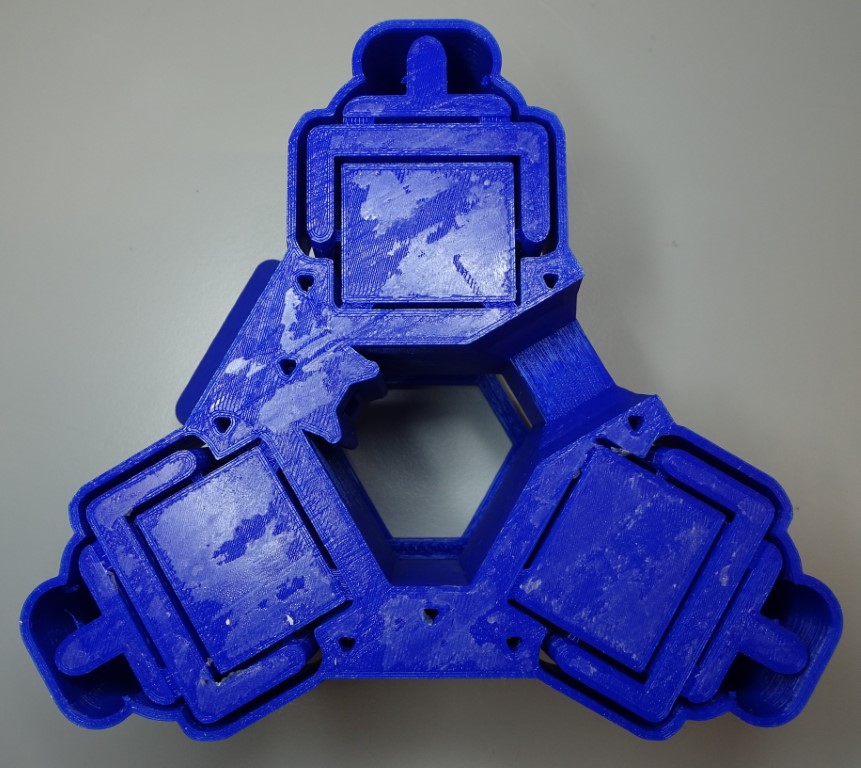
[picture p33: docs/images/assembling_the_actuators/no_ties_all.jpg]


## Assemble gear {pagestep}

Put a [M3x25mm hex head screw]{qty:3} into one [large gear]{qty:3}.
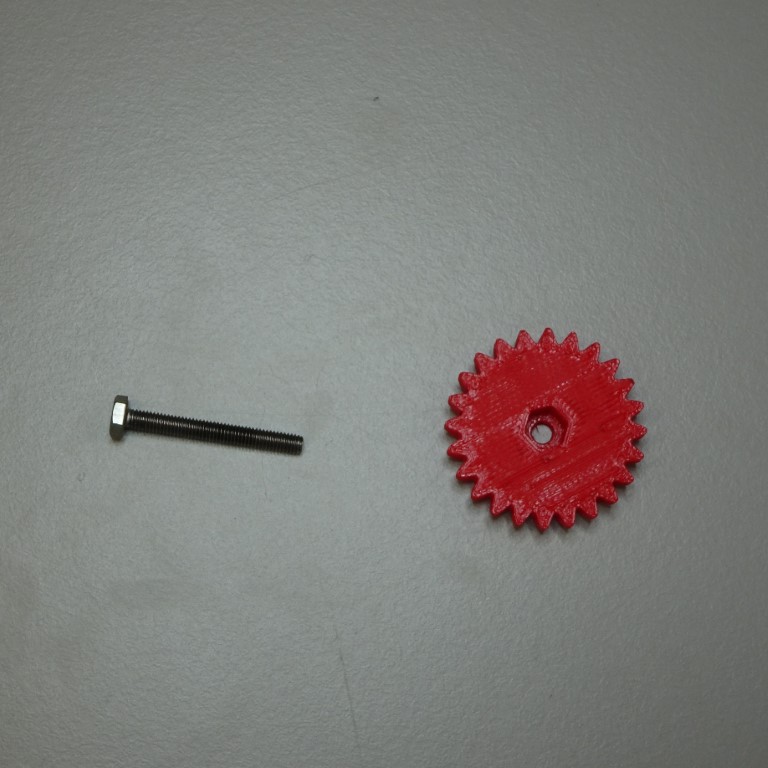
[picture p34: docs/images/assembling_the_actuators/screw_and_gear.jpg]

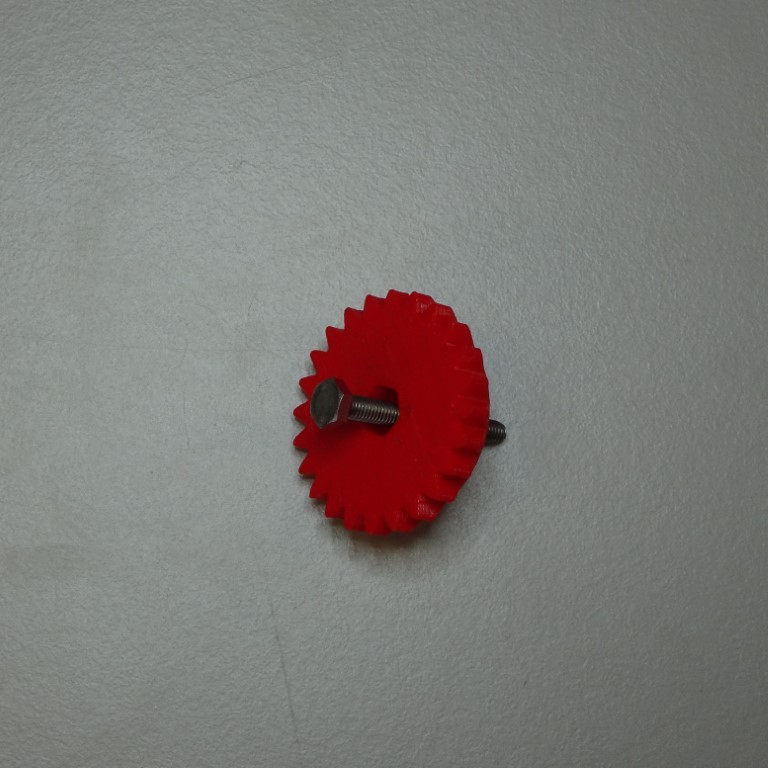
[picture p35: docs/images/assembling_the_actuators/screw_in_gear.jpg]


Put two [M3 washer]{qty:6}s onto the screw.
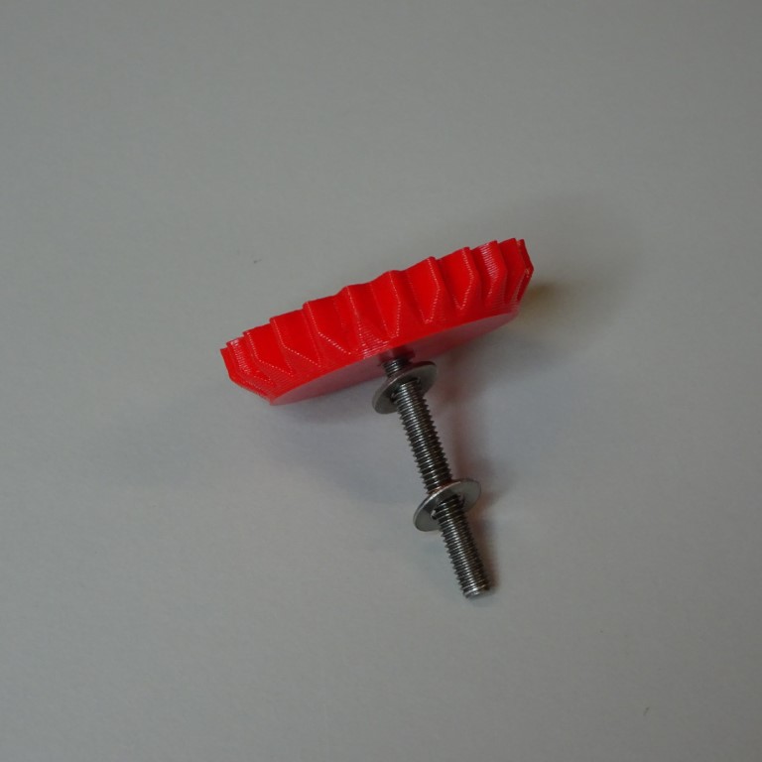
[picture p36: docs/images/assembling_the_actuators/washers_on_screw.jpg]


Repeat for all three gears.  

## Assemble actuator {pagestep}

Insert a [brass M3 nut]{qty:3} into the slot of one of the actuators, using the [nut tool]{qty:1}.
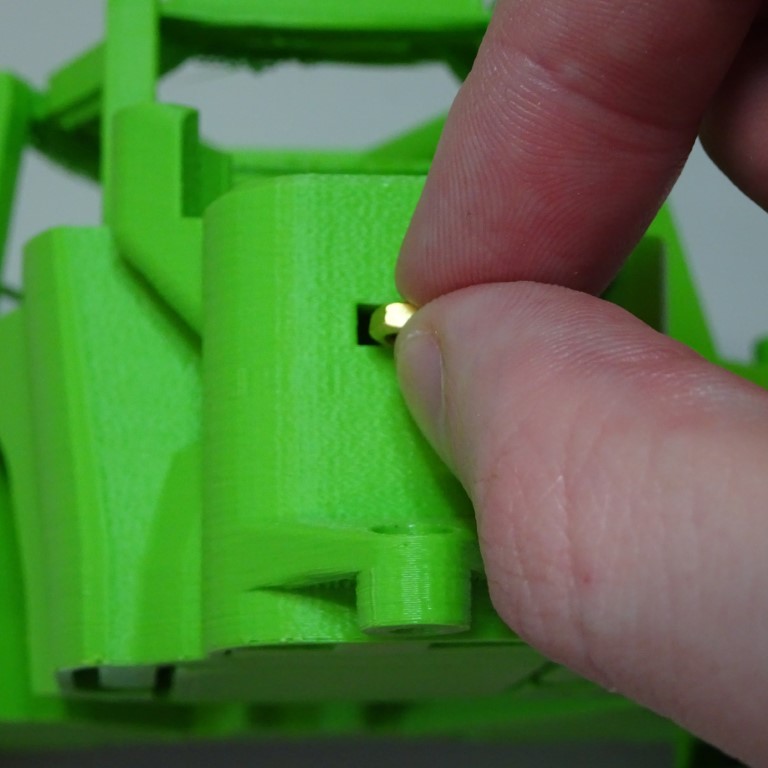
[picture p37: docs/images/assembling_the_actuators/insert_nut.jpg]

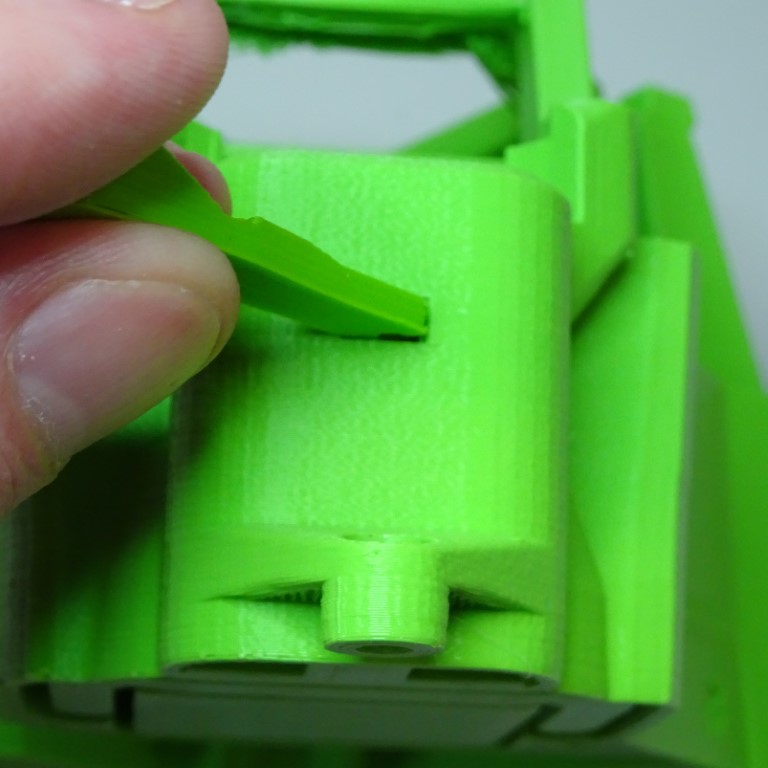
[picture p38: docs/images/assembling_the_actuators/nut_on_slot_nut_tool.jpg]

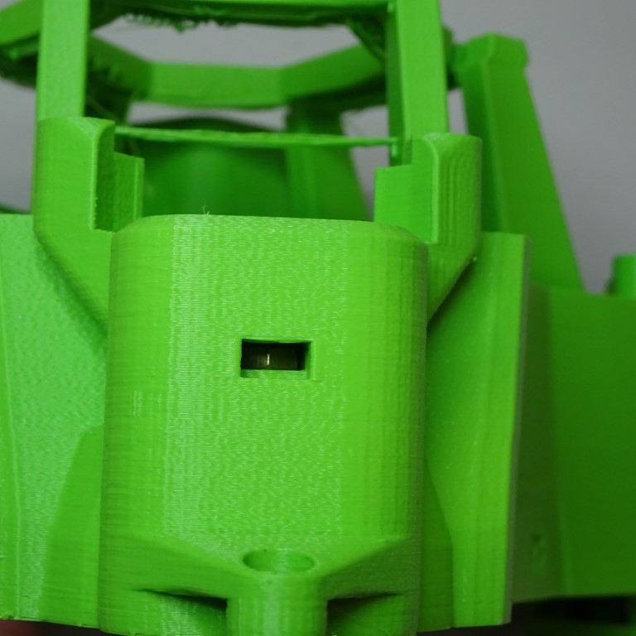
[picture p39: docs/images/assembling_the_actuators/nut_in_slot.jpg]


Screw the gear through the hole in the top of the actuator, through the nut that you just inserted.  Apply a small amount of [light oil]{qty:small amount} to the screw thread before it is fully tightened.
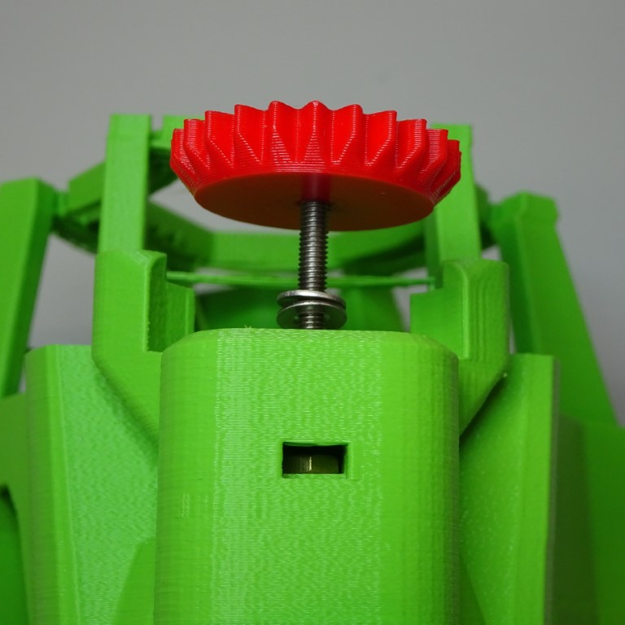
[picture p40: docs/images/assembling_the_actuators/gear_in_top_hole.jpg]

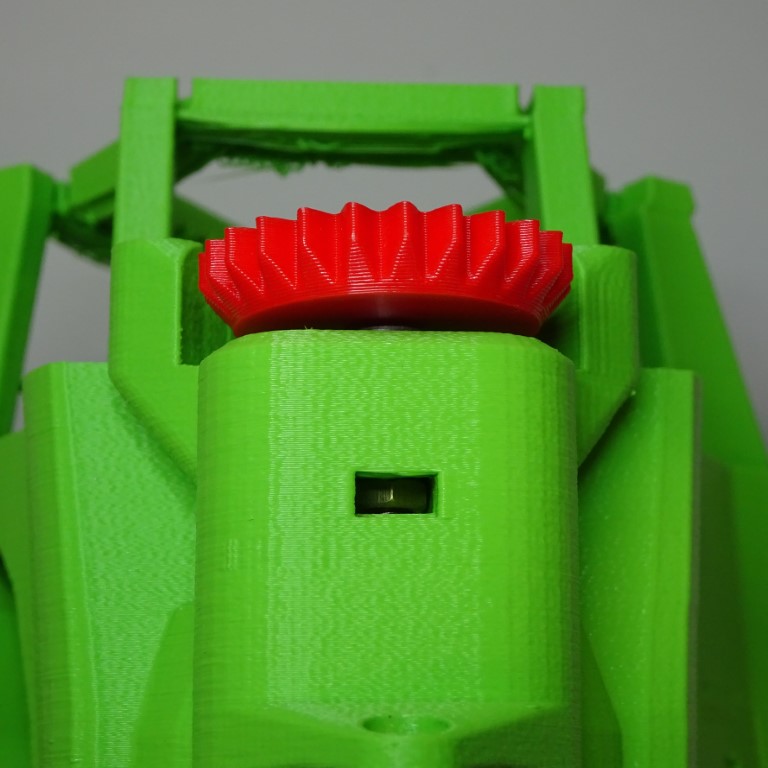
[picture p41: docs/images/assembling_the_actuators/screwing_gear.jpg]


Looking through the hole that the nut was pushed into, rotate the gear until you can see the hole inside align with the outside hole.  Push the [nut tool]{qty:1} into the hole so the column can't move.
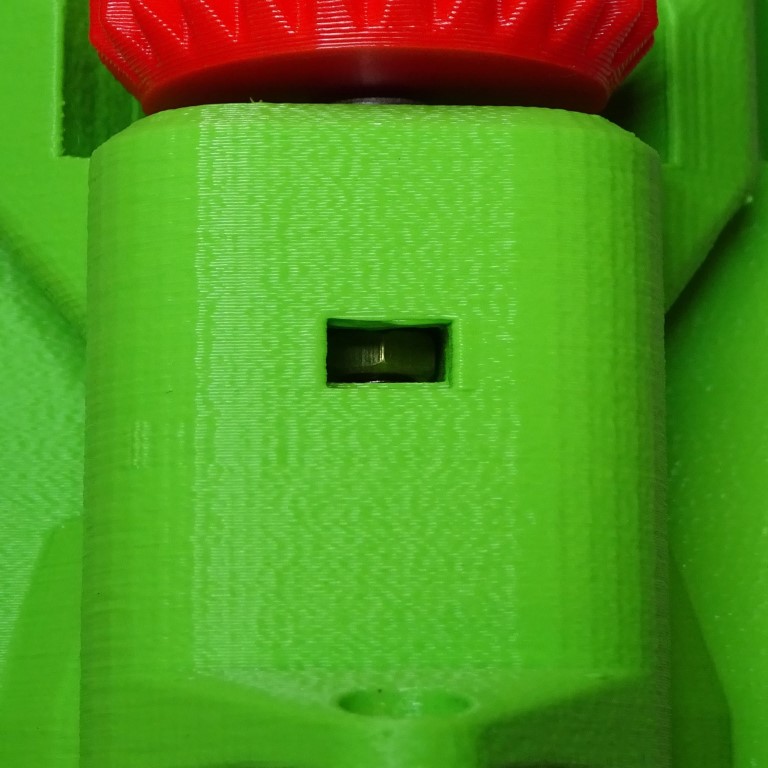
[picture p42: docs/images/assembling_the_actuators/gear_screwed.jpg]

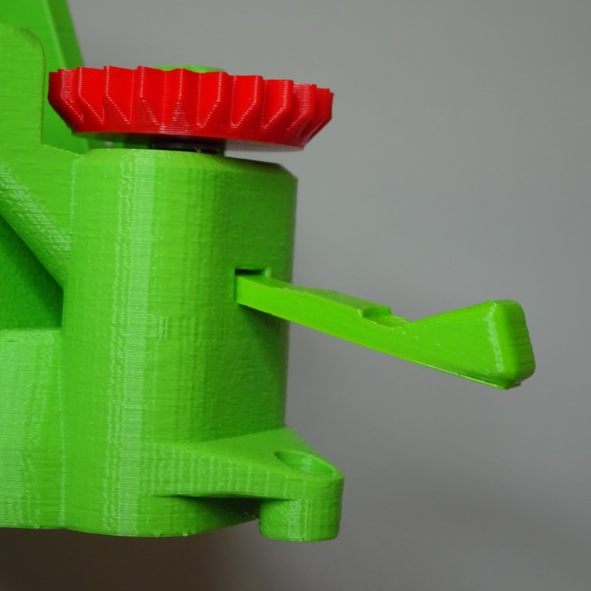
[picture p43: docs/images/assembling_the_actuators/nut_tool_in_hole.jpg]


Bend the [band tool]{qty:1} ready for use and put inside the [band tool holder]{qty:1}.
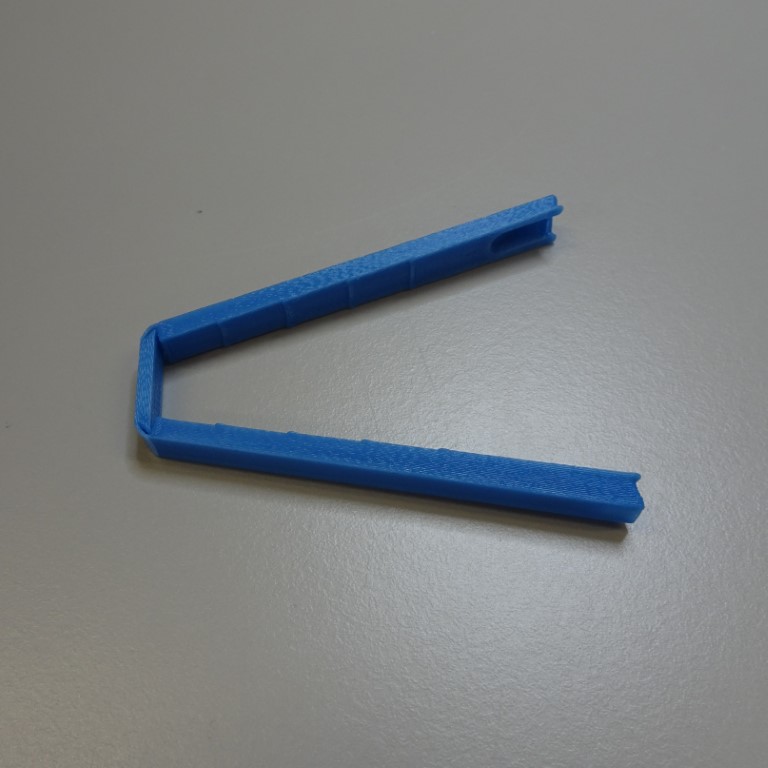
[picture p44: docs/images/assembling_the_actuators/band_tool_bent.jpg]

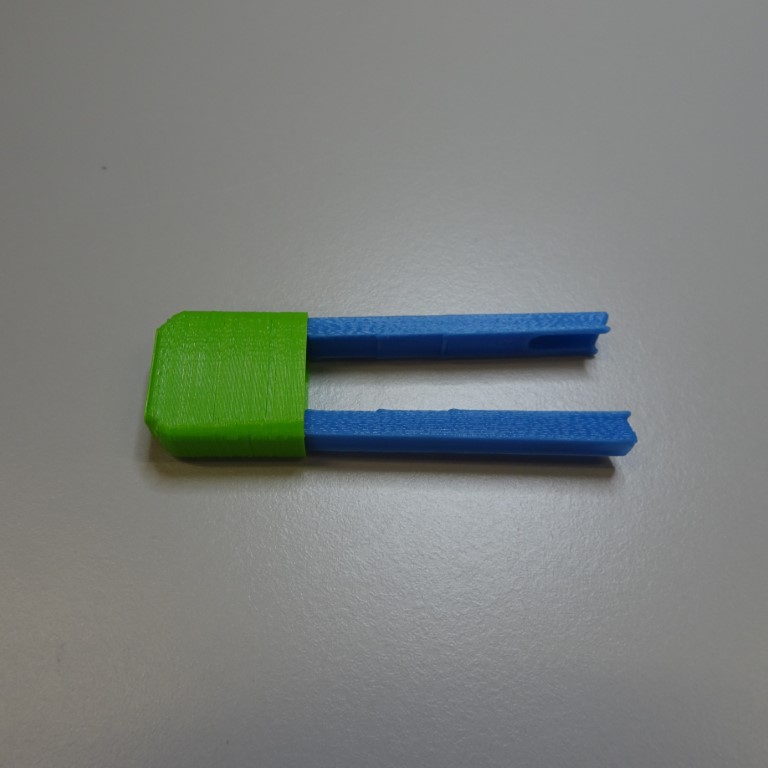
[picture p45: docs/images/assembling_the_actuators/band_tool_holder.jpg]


Attach one of the [feet]{qty:3} onto the bottom of the actuator.
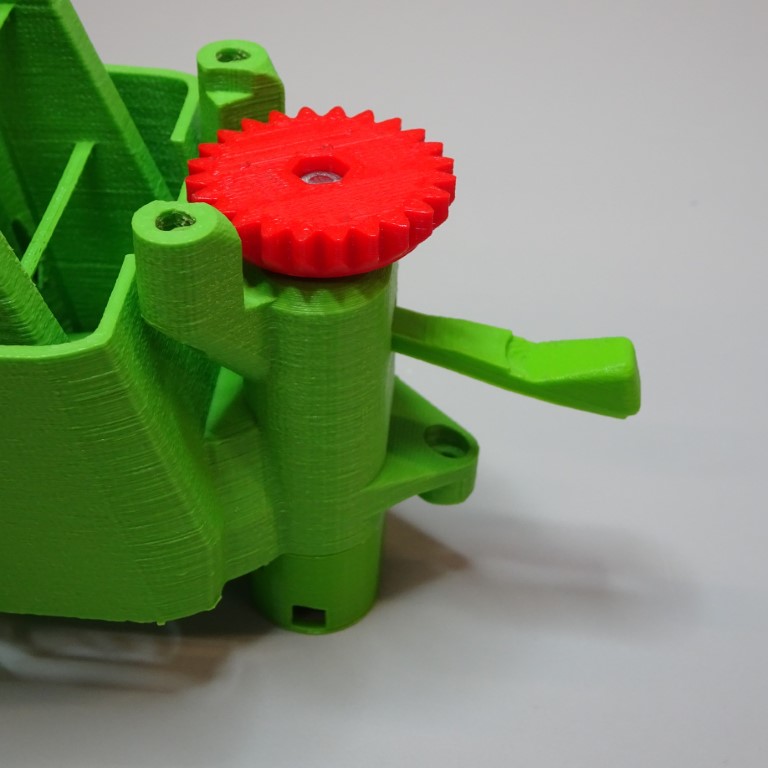
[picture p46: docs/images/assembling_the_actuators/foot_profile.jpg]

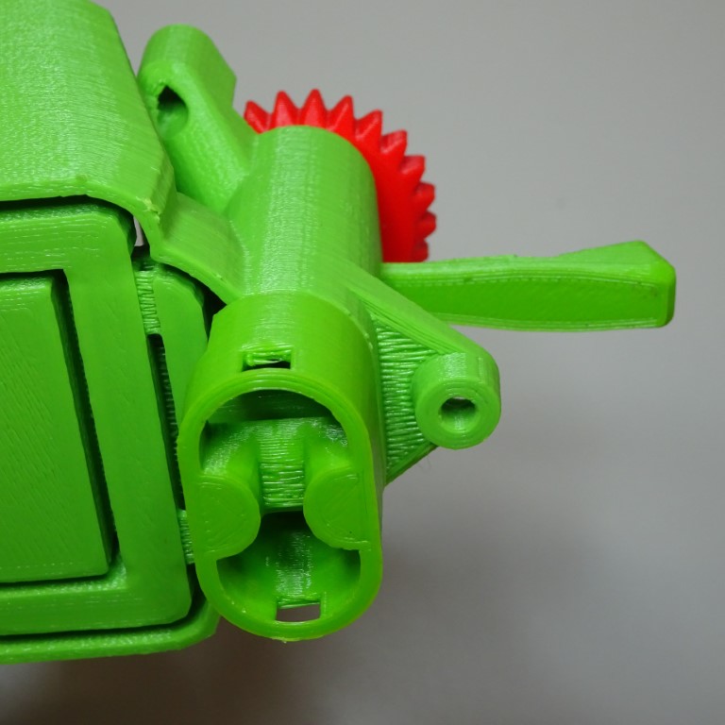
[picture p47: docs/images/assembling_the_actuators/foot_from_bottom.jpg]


Hold an [O-ring]{qty:3} against the bottom of the foot.  Push the [band tool] against the two sides of the [O-ring] so that the [O-ring] begins to enter the actuator.  Make sure the [O-ring] aligns with the grooves of the [band tool].  
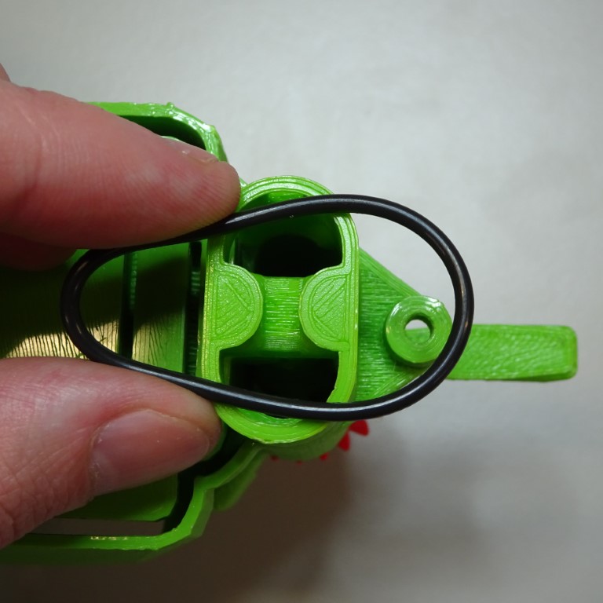
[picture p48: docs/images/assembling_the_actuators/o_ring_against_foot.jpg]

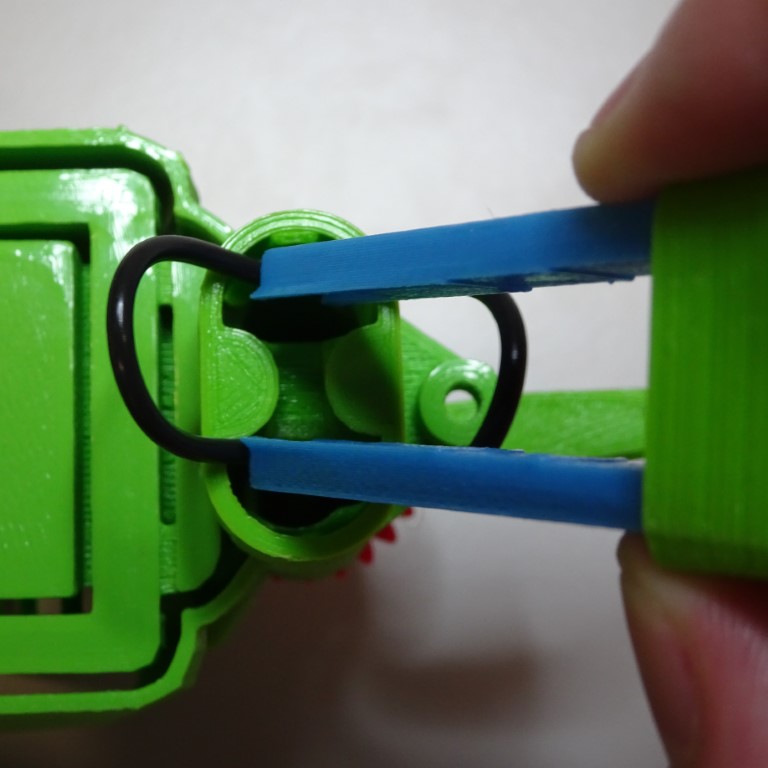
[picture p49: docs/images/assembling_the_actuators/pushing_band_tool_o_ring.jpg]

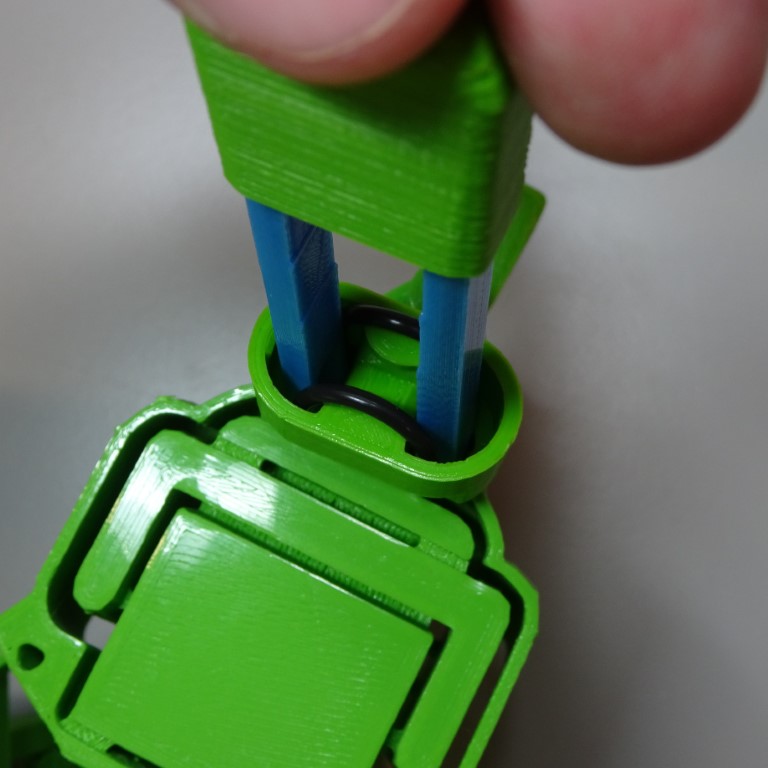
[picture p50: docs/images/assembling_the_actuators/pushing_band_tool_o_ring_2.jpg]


Push the [band tool] hard, forcing the [O-ring] further into the actuator, whilst making sure the [nut tool] stays in place.  Once you hear two clicks (the [O-ring] has been hooked at the top of the actuator), you can remove the [band tool] and [nut tool]. The [O-ring] and the actuator should stay in place.  If not, you may need to try again and push a little further.
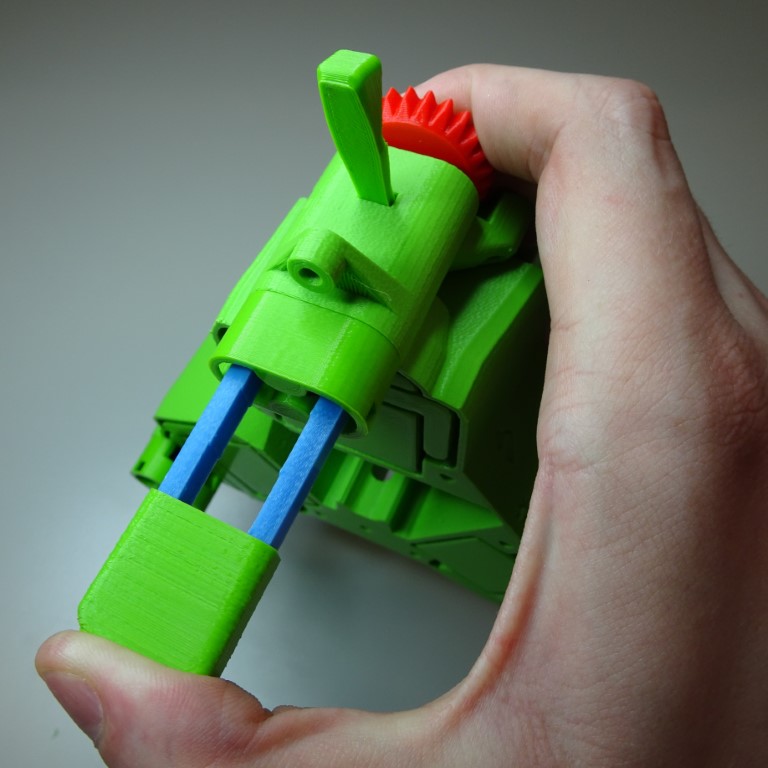
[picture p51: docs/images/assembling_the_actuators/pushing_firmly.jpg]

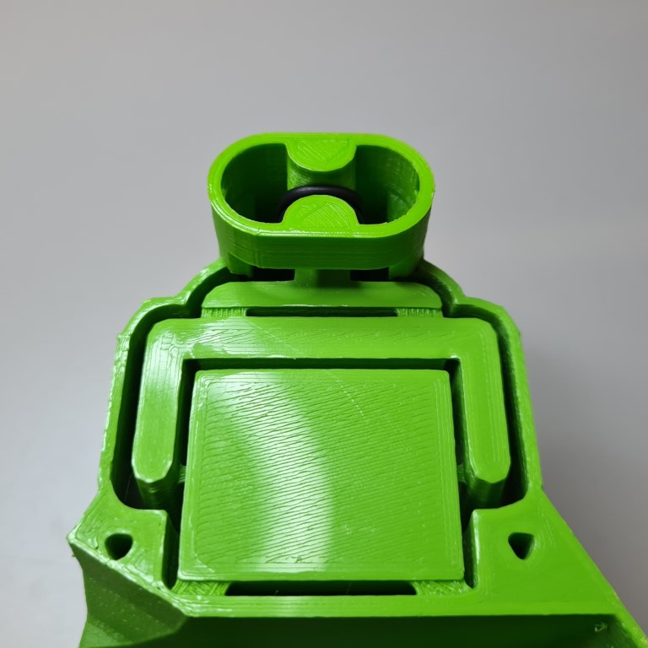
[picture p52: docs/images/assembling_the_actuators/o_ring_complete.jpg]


Repeat this step for all three actuators.
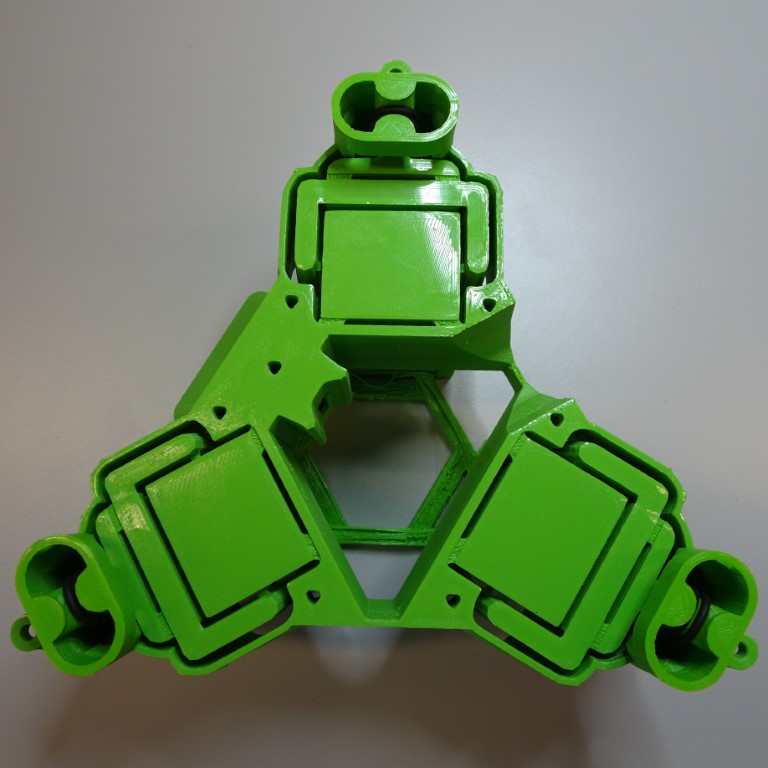
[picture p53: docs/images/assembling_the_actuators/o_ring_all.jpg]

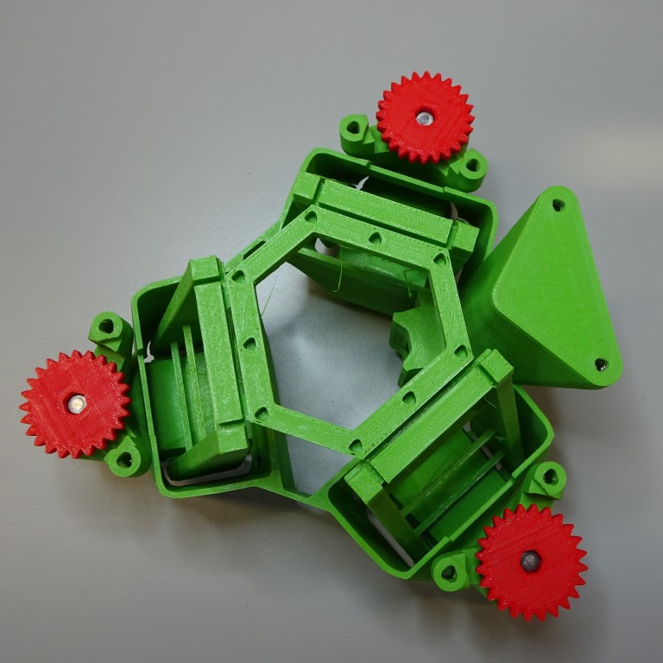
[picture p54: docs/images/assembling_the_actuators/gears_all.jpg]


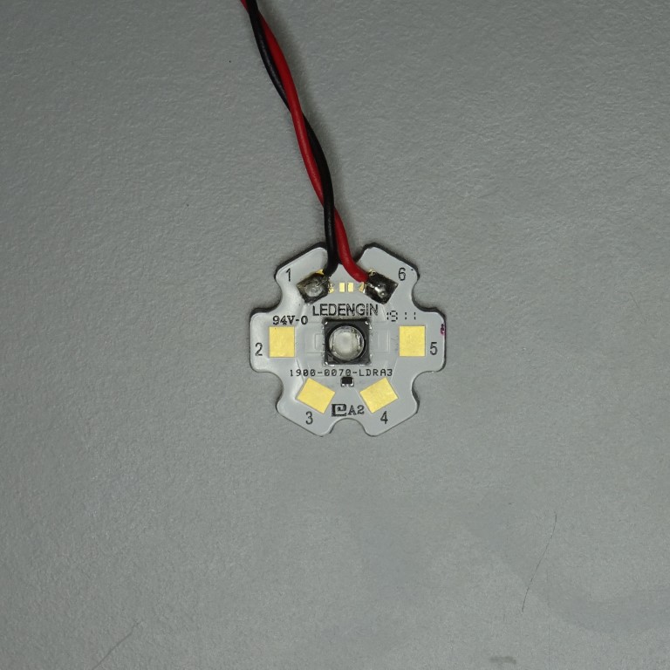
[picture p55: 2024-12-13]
docs/images/reflection_illumination/star_LED_solder.jpg

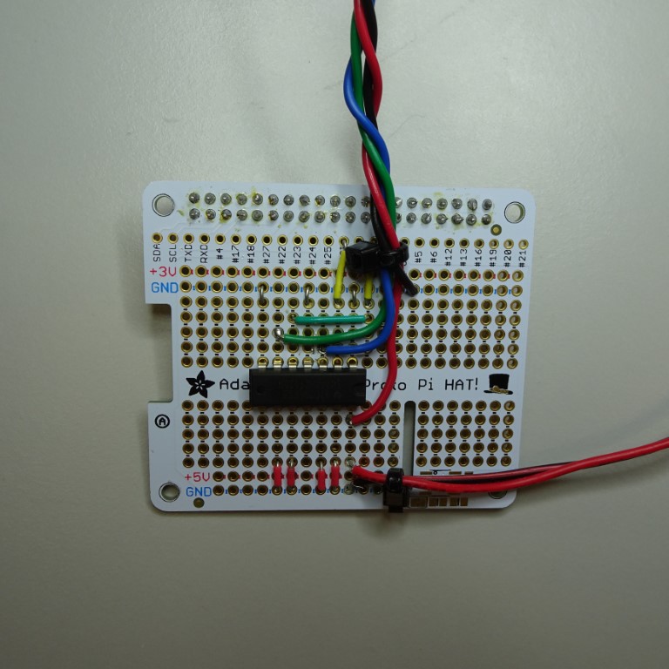
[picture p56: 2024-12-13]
docs/images/LED_grid_illumination/solder5.jpg

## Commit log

2018-02-20 initial commit
    Copied in the basic structure from the block stage and put together a basic delta bot structure.
    [compact_nut_seat.scad, delta_stage.scad, logo.scad, main_body.scad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]
2018-02-21 Added a casing in the style of the block stage
    [compact_nut_seat.scad, delta_stage.scad, parameters.scad, utilities.scad]
2018-02-21 Tweaks to the casing
    [delta_stage.scad]
2018-02-25 added mount for optics
    mount will probably put the optics way too low...
    [delta_stage.scad, utilities.scad]
2019-07-23 Switched from pasted-in files to using submodule
    [compact_nut_seat.scad, logo.scad, oshw_gear.dxf, utilities.scad]
2019-07-23 fixed import paths to use submodule
    [delta_stage.scad]
2019-07-31 Added feet specific to delta stage
    [feet.scad]
2019-07-31 removed old main body
    [main_body.scad]
2019-07-31 Added feet params
    [parameters.scad]
2019-07-31 Load default microscope params before delta-specific params
    [delta_stage.scad]
2019-07-31 Started draft of bucket base
    [base.scad]
2019-07-31 Added supports for feet
    [base.scad]
2019-08-01 Updated to new optics clip
    [delta_stage.scad]
2019-08-01 Updated to new dimensions
    [parameters.scad]
2019-08-01 Added windows to bucket base
    [base.scad]
2019-08-01 Fixed parameters
    [base.scad, delta_stage.scad, feet.scad, parameters.scad]
2019-08-01 Re-added cutout tollerance
    [base.scad]
2019-08-01 Slightly nicer windows
    [base.scad]
2019-08-01 Re-added new z-axis
    [delta_stage.scad, z_axis.scad]
2019-08-02 Minor parameter tweaks
    [parameters.scad]
2019-08-05 Increased small gear cutout size
    [delta_stage.scad]
2019-08-05 Widened again for more stability
    [parameters.scad]
2019-11-12 Added mounting holes
    [delta_stage.scad, parameters.scad]
2019-11-12 Added an SVG of the bottom of the stage
    [bottom_of_stage.scad]
2020-02-11 removed confusing extra casing line
    [delta_stage.scad]
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2020-03-05 Add cutout for reflection illuminator
    [delta_stage.scad]
2020-03-09 Fixed reflection cutout width
    [delta_stage.scad, parameters.scad]
2020-07-05 Added access hole for objective screw
    [delta_stage.scad]
2020-07-06 remove objective mount screw access (no longer required)
    [delta_stage.scad]
2020-07-06 Improve and simplify the casing
    [delta_stage.scad, parameters.scad]
2020-07-06 Add a condenser mount
    [delta_stage.scad, parameters.scad]
2020-07-06 Move the objective back to the 60* position
    [delta_stage.scad]
2020-07-07 Add mounting holes for the stage
    [delta_stage.scad]
2020-07-07 Parameter for reflection_illumination
    [delta_stage.scad, parameters.scad]
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2020-07-09 Update build script for the different stage configurations and parts from the OFM repository
    Former-commit-id: 504595e7d8689c9460b1a7de399efc9bdc27ab9b
    [parameters.scad]
2020-07-09 Update base to match the new delta stage casing
    [base.scad]
2020-07-09 default configuration to basic stage
    [parameters.scad]
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2020-07-25 Made new base for raspberry pi and sangaboard
    [base _raspi_sangaboard.scad, delta_stage.scad, parameters.scad]
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2020-08-10 Commented and cleaned up base code
    [base_raspi_sangaboard.scad, parameters.scad]
2020-08-10 reduced casing height to improve print time
    [parameters.scad]
2020-08-10 Increase tolerance for gear
    [delta_stage.scad]
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2020-09-06 Added OSHW and OpenFlexure logos
    Former-commit-id: 54620571d7e9a810409b514046e9b5b6f3aa9deb
    [delta_stage.scad, parameters.scad]
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2020-10-07 Reduce depth of logos
    Former-commit-id: d78522e4b2c34ab52ceb850a180c38158716d950
    [delta_stage.scad]
2020-10-27 Move the mounting holes into separate modules
    Former-commit-id: 39fdc683790ea31a6f6f4a33436271009225b92c
    [delta_stage.scad]
2020-10-27 A generic base for stage adaptors.
    Former-commit-id: a033322da47930ddd66139141b95f3d9ec8e2c62
    [stage_adaptor_base.scad]
2020-10-27 A stage adaptor for a 35mm petri dish
    Former-commit-id: d3856877a1cad77df73f4209029bd326c23397a2
    [35mm_petri_dish_holder.scad]
2020-10-27 A stage adaptor for a 35mm petri dish
    Former-commit-id: 06ae5f1f061da285e53c64139d3ec9f4a50405d7
    [35mm_petri_dish_holder.scad]
2020-10-27 Update 35mm_petri_dish_holder.scad
    Former-commit-id: 9db3449cea53c5008dfcf6212fb37c428ff6a380
    [35mm_petri_dish_holder.scad]
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2020-11-21 Vent holes for Raspberry Pi
    Former-commit-id: a6f154e3d14bbdce511e46aa922d85b0d95c2ad1
    [base_raspi_sangaboard.scad]
2020-11-21 Access slot for SD card
    Former-commit-id: b11ffc8b6e39b6652a2441add00035af0792f5b4
    [base_raspi_sangaboard.scad]
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2020-11-24 Move condenser mount and objective bolt slot to new module
    Former-commit-id: e51d784e29e42b2591cb2ddc0d8fd8bea8227ef0
    [delta_stage.scad]
2020-11-24 Simplify hollowed out space in center and increase size
    Former-commit-id: 7c8b563bac0651deaddd437c668207ea0bf54bcd
    [delta_stage.scad]
2020-11-24 Improve bridging for fl cutout
    Former-commit-id: 44a7c372726089372e9a24a3b62bab83f0207eb7
    [delta_stage.scad]
2020-11-24 Fix gap for objective mount to body
    Former-commit-id: 34b1db2438a905f9f019948b2d81926603fbe4de
    [delta_stage.scad]
2020-11-24 Move legs to separate module
    Former-commit-id: a3e9a503c2b2578dcc6f42956329222163958d78
    [delta_stage.scad]
2020-11-24 formatting fixes
    Former-commit-id: 93fe49429277871902eb3ab16c62971eea1eb6d9
    [delta_stage.scad]
2020-11-25 Move base of condenser back
    Former-commit-id: 52eed41513837e08f5e2d110c1637f4309975ad1
    [delta_stage.scad]
2020-11-28 Add Delta stage logo
    Former-commit-id: cd1721f7c76e72f8a3fae42918bbcb451ea8acb2
    [delta_stage_logo.scad, openflexure_delta_stage_logo.dxf]
2020-11-28 Rename condenser_mount to transmission_illumination
    Former-commit-id: cfd7ba4632733a67da23b199ce7653c26d28dad6
    [parameters.scad]
2020-11-28 Add new delta stage logo
    Former-commit-id: c381c3f73f193f02a70901f01c5ecc2d834c094f
    [delta_stage.scad]
2020-11-28 Fix merge error
    Former-commit-id: e575f6283445addb95d38dbdc171c17b9d5132d4
    [delta_stage.scad]
2020-11-28 Rename condenser_mount to transmission_illumination
    Former-commit-id: 653393a8fcf4d42d9ac839f5f20198b168c4b5f8
    [delta_stage.scad]
2020-11-28 Formatting
    Former-commit-id: a1d8fb6460154e4f0b95003fe937c3018cbd853a
    [delta_stage.scad]
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2020-11-29 objective bolt access slot in condenser mount
    Former-commit-id: 7d2126a389b1fb8373ec339953d3d29c90371353
    [delta_stage.scad]
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2020-11-30 Fix rebase error
    Former-commit-id: 0e40d15e787581f11f21785daad45cd591c69937
    [delta_stage.scad]
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2020-12-04 use an exterior brim
    Former-commit-id: 477f9e286a539dfca3d8ec3ec63e4986dd9369fc
    [delta_stage.scad]
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2020-12-14 Fritzing for LED grid
    Former-commit-id: aaf82598006987aa1bca60a268d24d9e1cd44ed3 [formerly e844e490937f78223bc0007f393fc236317dd8c9] [formerly e8f1510b648590257625887b04747bdf15f5d6d1 [formerly a782546b88818bc65bb9f1b4c2f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
    [LED_grid.fzz]
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2020-12-16 No brim by default
    Former-commit-id: c91a77a15e772a6c22aace013cd70c4142385971 [formerly 204f8fc2530f30ca3d2b83189ff9f9a95c5b36c0] [formerly 09a061e964589e9358eada02635901d7f0034d49 [formerly 0f390c58bf1a9b42c1eeb32cdb4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
    [delta_stage.scad]
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2021-02-23 Separate out the simple base height.
    Former-commit-id: 2dcfe0931b805e915a8e119c8c516f7e75b1fcae [formerly c30468c04336e2aeecba8af94c29f2d4c383d196] [formerly 53df90f382a14d7a813a0a335482f8edc19096fd [formerly a9d03400ed6a8fe551294945370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
    [base.scad, parameters.scad]
2021-02-23 fix base height parameters.scad
    Former-commit-id: 03f2f331ff66dbf580276935dbb2605ea8f145c1 [formerly 0b680d2fa519365671c91530997b68d26b3bc426] [formerly 0249dcc22b57cd6b1d3b9b5a279112e65d240ae1 [formerly 3b57212cf35eeff56ab845c3286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
    [parameters.scad]
2021-03-01 Update version numstring to 1.0.1
    Former-commit-id: 770e8dc8a4eaafd672aead63402b099fc6e5baa1 [formerly cd054e307b2eeff8ce3f3aaf6eb1b34a5bf11746] [formerly 95f077c09fe2be4f909eaa88573c9438f1091651 [formerly 7000bc0653259a942d920ea029c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
    [parameters.scad]
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2021-04-22 Add mounting points for base to main body
    [delta_stage.scad]
2021-04-22 Swap the positions of the logos
    [delta_stage.scad]
2021-04-22 Remove accidentally repeated code
    [delta_stage.scad]
2021-04-22 Add the base mounting point radius
    [parameters.scad]
2021-04-22 Add logos to base
    [base_raspi_sangaboard.scad]
2021-04-22 Change sangaboard window to full width of power_HDMI_window
    [parameters.scad]
2021-04-22 Increase depth of top cutouts and add new cutout
    [base_raspi_sangaboard.scad]
2021-04-22 change foot stands to be overhangs
    [base_raspi_sangaboard.scad]
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2021-04-23 Make height of foot stands correct
    [base_raspi_sangaboard.scad]
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2021-05-18 Fix incorrect order of commands
    [base_raspi_sangaboard.scad]
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2021-07-02 Correct dimensions
    [55mm_petri_dish_holder.scad]
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2021-08-16 Revert "Version bump"
    This reverts commit 3d814ea23a9d7463cf8f899fc088d1f772924b7e
    [parameters.scad]
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
